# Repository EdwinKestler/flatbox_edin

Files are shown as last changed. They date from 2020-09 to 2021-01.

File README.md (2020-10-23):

# flatbox_edin
Remote math inclusive education for the vision impaired

This is our first attempt to bring remote math edcuation to vision impaired persons. 

#IoT to empower humans. 

Hardware: Raspberry pi 4, 4GB Gateway paired via Wifi to Haptic interfase (drv2603) with response mechanism (MAX6817 de bounce) (vibration motors and push buttons) 2 units. 
IoT: JSON, MQTT, WiFi.
Software: Rabbit MQ, Node-Red, Maria DB, Node.js Angular 9
Cloud: Goolge cloud-> BigQuery, Pub/Sub, Cloud Functions (python and Node.js) 

Main Idea: so a teacher can remotely teach math  to many vision imparied studentes. 1 to many or 1 to 1, via the internet and aremote conference call
Techers interface:
Watch the video (https://youtu.be/AhM5wchl2cA)
Basic Hardware interface:
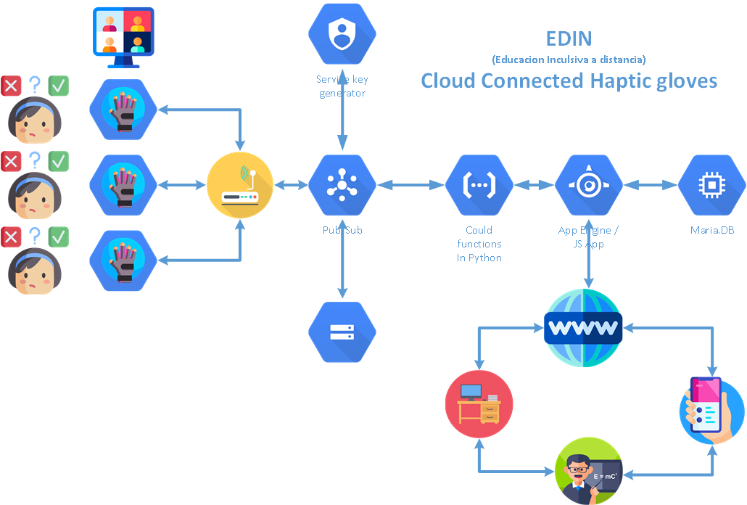
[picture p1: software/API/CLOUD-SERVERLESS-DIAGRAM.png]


Licencing:

Software: 


Hardware: License: <tspan y="0" x="71.357224" id="tspan1179">CERN-OHL-1.2</tspan></text></g></g><text id="text1788" y="-45.219803" x="138.91757" style="font-style:normal;font-weight:normal;font-size:40.0001px;line-height:1.25;font-family:sans-serif;fill:#000000;fill-opacity:1;stroke:none;stroke-width:1" xml:space="preserve">
  
Documentation: 


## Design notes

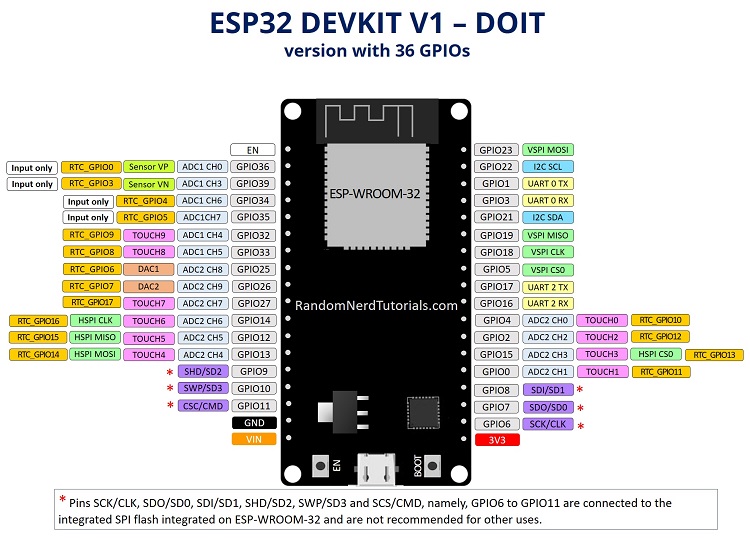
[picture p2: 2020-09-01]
imagenes/ESP32-DOIT-DEVKIT-V1-Board-Pinout-36-GPIOs-updated.jpg

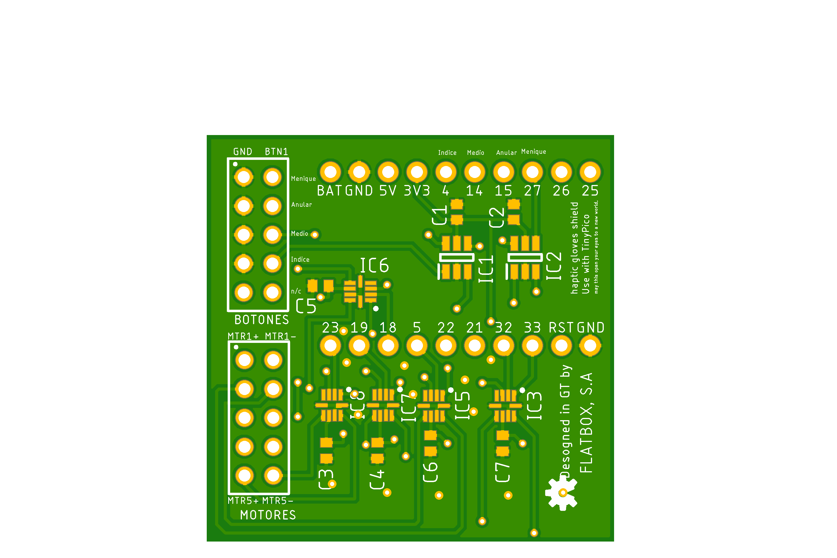
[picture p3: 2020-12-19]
Hardware/Edin_DRV203/Eagle/Shield_Empty.png

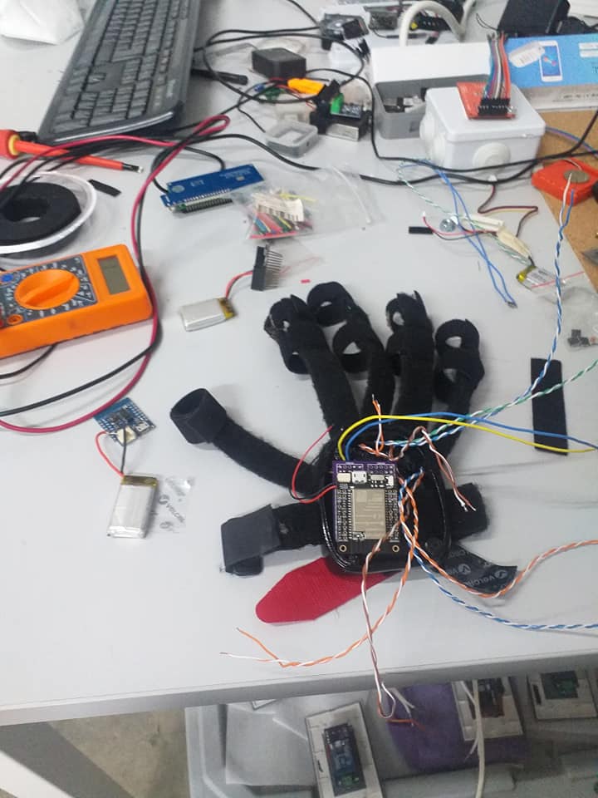
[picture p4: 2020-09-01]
imagenes/117703259_10159825911758132_3864473577027789279_n.jpg

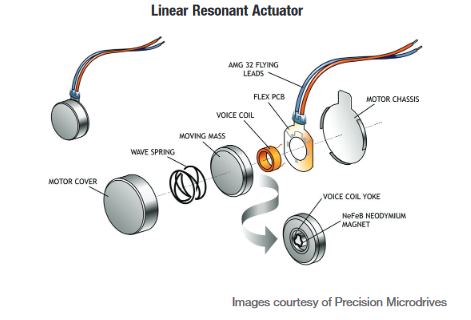
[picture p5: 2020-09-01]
imagenes/haptic-fig-5.webp

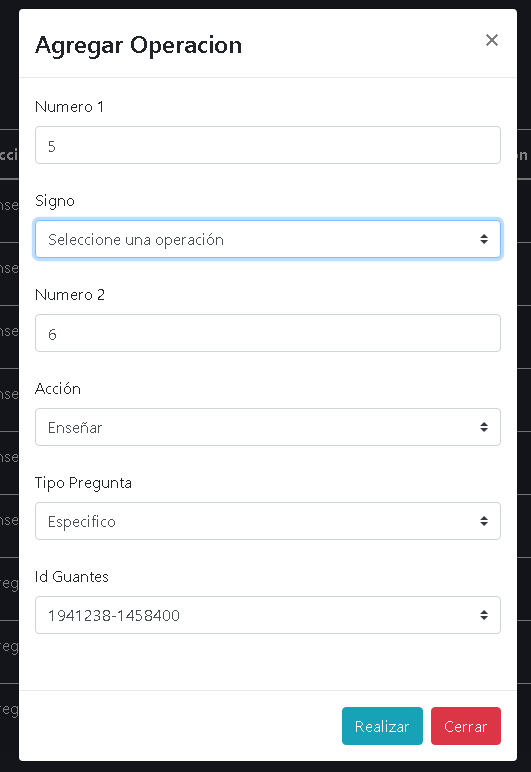
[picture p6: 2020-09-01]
imagenes/operaciones.PNG

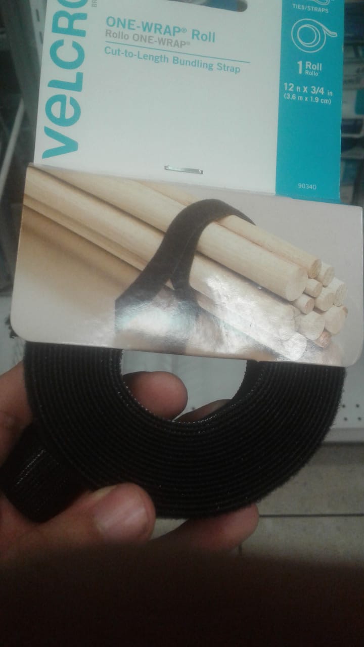
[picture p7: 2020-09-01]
imagenes/b04c229d-c1c4-4ab2-8d0b-719aa09d2a6d.jpg

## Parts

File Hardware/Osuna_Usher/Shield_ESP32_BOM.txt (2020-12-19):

Partlist

Exported from Esp32_Shield.brd at 20/01/2020 19:34

EAGLE Version 9.5.0 Copyright (c) 1988-2019 Autodesk, Inc.

Assembly variant: 

Part     Value                    Package     Library                 Position (mil)        Orientation

BOTONES  BTN 10 PIN               61301021821 Wurth_Connectors_WR-PHD (160 860)             R90
C1_MÑQ   0.1uF                    C0805       resistor                (-950 910)            R90
C2_MDO   0.1uF                    C0805       resistor                (-770 1280)           R180
C3_ANL   0.1uF                    C0805       resistor                (-60 1650)            R180
C4_PLG   0.1uF                    C0805       resistor                (-560 920)            R90
C5_IND   0.1uF                    C0805       resistor                (-960 1220)           R270
D1_B     BLUE                     LED-1206    SparkFun-LED            (-1090 1110)          R180
D2_ANL   1N4148WS                 SOD-323     Diodes                  (-130 1430)           R270
D2_G     GREEN                    LED-1206    SparkFun-LED            (-1090 1030)          R180
D2_MÑQ   1N4148WS                 SOD-323     Diodes                  (-760 980)            R0
D2_PLG   1N4148WS                 SOD-323     Diodes                  (-390 980)            R0
D3_IND   1N4148WS                 SOD-323     Diodes                  (-790 1060)           R0
D3_MDO   1N4148WS                 SOD-323     Diodes                  (-570 1180)           R0
D3_R     RED                      LED-1206    SparkFun-LED            (-1090 950)           R180
MOTORES  MTR 10 PIN               61301021821 Wurth_Connectors_WR-PHD (160 1500)            R270
R1       1K                       R0805       resistor                (-1230 1490)          R90
R2       1K                       R0805       resistor                (-950 1480)           R90
R3       1K                       R0805       resistor                (-650 1480)           R90
R4       1K                       R0805       resistor                (-420 1480)           R90
R5       1K                       R0805       resistor                (-390 1180)           R270
R6_IND   1K                       R0805       resistor                (-780 1160)           R180
R6_R     220                      R0805       resistor                (-1190 870)           R0
R7_G     220                      R0805       resistor                (-1190 1300)          R0
R7_PLG   1K                       R0805       resistor                (-380 890)            R180
R8_B     220                      R0805       resistor                (-1190 1210)          R0
R8_MÑQ   1K                       R0805       resistor                (-760 880)            R180
R9_MDO   1K                       R0805       resistor                (-570 1280)           R180
R10_ANL  1K                       R0805       resistor                (-20 1440)            R90
R13_MÑQ  10K                      R0805       resistor                (-110 600)            R0
R14_MDO  10K                      R0805       resistor                (-110 860)            R0
R15_IND  10K                      R0805       resistor                (-110 990)            R0
R16_ANL  10K                      R0805       resistor                (-110 730)            R0
R17_PLG  10K                      R0805       resistor                (-110 1120)           R0
SV5      ESP32 2x10 PIN_DERECHO   61302021821 Wurth_Connectors_WR-PHD (-750 1700)           R180
SV6      ESP32 2x10 PIN_IZQUIERDO 61302021821 Wurth_Connectors_WR-PHD (-750 700)            R180
T1       600mA/40V                SOT23-3     SparkFun-DiscreteSemi   (-1110 1420)          R270
T2       600mA/40V                SOT23-3     SparkFun-DiscreteSemi   (-830 1400)           R270
T3       600mA/40V                SOT23-3     SparkFun-DiscreteSemi   (-540 1400)           R270
T4       600mA/40V                SOT23-3     SparkFun-DiscreteSemi   (-300 1400)           R270
T5       600mA/40V                SOT23-3     SparkFun-DiscreteSemi   (-260 1260)           R0

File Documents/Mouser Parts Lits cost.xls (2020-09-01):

EDIN-USHERV2.0
Mouser # | Mfr. # | Manufacturer | Customer # | Description | RoHS | Lifecycle | Order Qty. | Price (USD) | Ext.: (USD)
581-06031C104KAT2A | 06031C104KAT2A | AVX |  | Multilayer Ceramic Capacitors MLCC - SMD/SMT 100V 0.1uF 0603 X7R 10% | RoHS Compliant |  | 2 | $0.19 | $0.38
791-0603B104K160CT | 0603B104K160CT | Walsin |  | Multilayer Ceramic Capacitors MLCC - SMD/SMT 0.1uF 16V 10% 0805 X7R | RoHS Compliant | New At Mouser | 5 | $0.10 | $0.50
700-MAX6817EUTT | MAX6817EUT+T | Maxim Integrated |  | Supervisory Circuits A +/- 15kV ESD-Protected, Single/Dual/Octal, CMOS Switch Debouncers | RoHS Compliant |  | 2 | $4.32 | $8.64
595-DRV2603RUNR | DRV2603RUNR | Texas Instruments |  | Motor / Motion / Ignition Controllers & Drivers Haptic Driver w/Auto Resonance Tracking | RoHS Compliant |  | 5 | $1.31 | $6.55

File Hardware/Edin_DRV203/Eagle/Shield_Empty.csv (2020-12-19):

Qty | Value | Device | Package | Parts | Description | DATASHEET-URL | DESCRIPTION | GENDER | HEIGHT | IR | MANUFACTURER_NAME | MANUFACTURER_PART_NUMBER | MATES | MOUSER_PART_NUMBER | MOUSER_PRICE-STOCK | PACKAGING | PART-NUMBER | PINS | PROD_ID | ROWS | TYPE
2 |  | TINYPICO_HEADER_10NO_SILK_PTH_FEMALE | 1X10_NO_SILK | LEFT, RIGHT | Multi connection point. Often used as Generic Header-pin footprint for 0.1 inch spaced/style header connections |  |  |  |  |  |  |  |  |  |  |  |  |  | CONN-11563
5 | 06031C104KAT2A | 06031C104KAT2A | CAPC1608X90N | C3, C4, C5, C6, C7 | AVX - 06031C104KAT2A - CAP, MLCC, X7R, 0.1UF, 100V, 0603 |  | AVX - 06031C104KAT2A - CAP, MLCC, X7R, 0.1UF, 100V, 0603 |  | 0.9mm |  | AVX | 06031C104KAT2A |  | 581-06031C104KAT2A | https://www.mouser.co.uk/ProductDetail/AVX/06031C104KAT2A?qs=oF%2FSscNnLpBUv12UcNAw2A%3D%3D
2 | 0603B104K160CT | 0603B104K160CT | CAPC1608X87N | C1, C2 | WALSIN - 0603B104K160CT - CAP, 0.1F, 16V, 10%, X7R, 0603 |  | WALSIN - 0603B104K160CT - CAP, 0.1F, 16V, 10%, X7R, 0603 |  | 0.87mm |  | Walsin Technology Corporation | 0603B104K160CT |  | 791-0603B104K160CT | https://www.mouser.com/Search/Refine.aspx?Keyword=791-0603B104K160CT
1 | BTN 10 PIN | 6130XX21821_61301021821 | 61301021821 | BOTONES | WR-PHD 2.54 mm Dual Socket Header | https://katalog.we-online.com/em/datasheet/61301021821.pdf |  | Socket Header |  | 3A |  |  | WR-PHD 2.54mm SMT Dual Pin Header/THT Angled Dual Pin Header/THT Dual Board Stacker/THT Dual Pin Header |  |  | Tray | 61301021821 | 10 |  | Dual | Straight
5 | DRV2603RUNR | DRV2603RUNR | QFN50P200X200X80-10N | IC3, IC5, IC6, IC7, IC8 | Haptic Driver with Auto Resonance Tracking for LRA and Optimized Drive for ERM |  | Haptic Driver with Auto Resonance Tracking for LRA and Optimized Drive for ERM |  | 0.8mm |  | Texas Instruments | DRV2603RUNR |  | 595-DRV2603RUNR | https://www.mouser.co.uk/ProductDetail/Texas-Instruments/DRV2603RUNR?qs=l6ZoeTYLMwNhoGl8Q31%2FaA%3D%3D
2 | MAX6817EUT+T | MAX6817EUT+T | SOT95P280X145-6N | IC1, IC2 | Supervisory Circuits Dual Switch Debouncer |  | Supervisory Circuits Dual Switch Debouncer |  | 1.45mm |  | Maxim Integrated | MAX6817EUT+T |  | 700-MAX6817EUTT | https://www.mouser.co.uk/ProductDetail/Maxim-Integrated/MAX6817EUT%2bT?qs=1THa7WoU59HkU%2FfQtsyW%252BA%3D%3D
1 | MTR 10 PIN | 6130XX21821_61301021821 | 61301021821 | MOTORES | WR-PHD 2.54 mm Dual Socket Header | https://katalog.we-online.com/em/datasheet/61301021821.pdf |  | Socket Header |  | 3A |  |  | WR-PHD 2.54mm SMT Dual Pin Header/THT Angled Dual Pin Header/THT Dual Board Stacker/THT Dual Pin Header |  |  | Tray | 61301021821 | 10 |  | Dual | Straight
1 | OSHW-LOGOS | OSHW-LOGOS | OSHW-LOGO-S | LOGO1 | Open-Source Hardware (OSHW) Logo

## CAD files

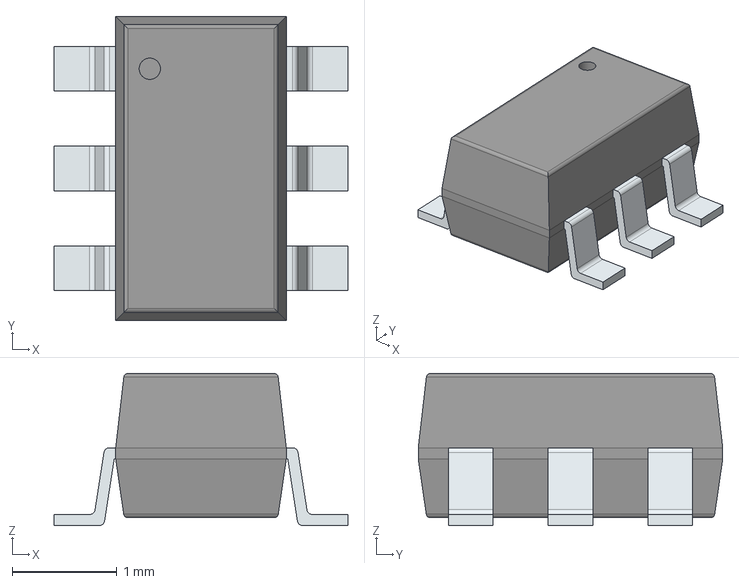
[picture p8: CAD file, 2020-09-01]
EcadModels/MAX6817EUT+T/3D/MAX6817EUT+T.stp
2.80 x 2.90 x 1.45 mm
PinsArrayLR

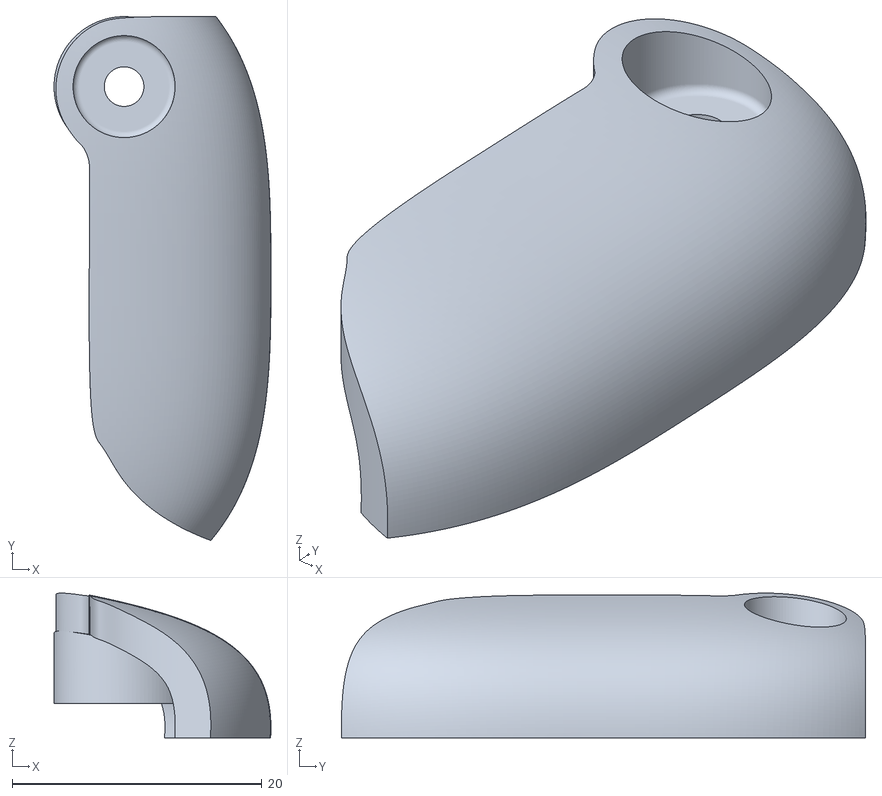
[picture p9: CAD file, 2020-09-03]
Fusion Models/EDIN_Tapadera.stl
17.4 x 42.0 x 11.6

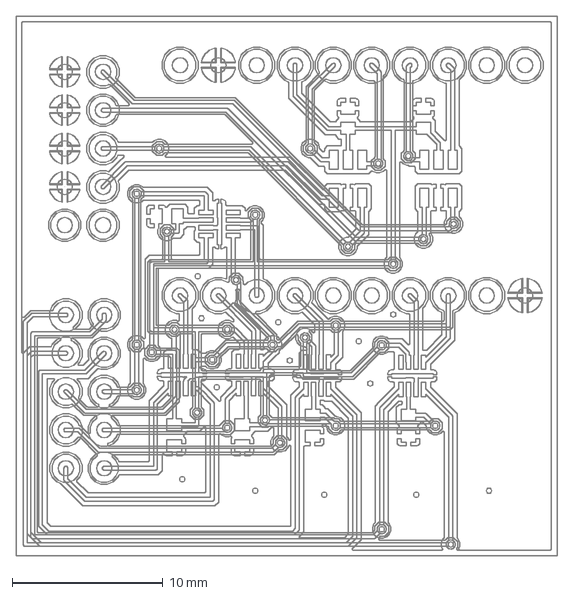
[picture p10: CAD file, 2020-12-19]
Hardware/Edin_DRV203/Eagle/Shield_Empty.dxf
35.9 x 35.8 mm

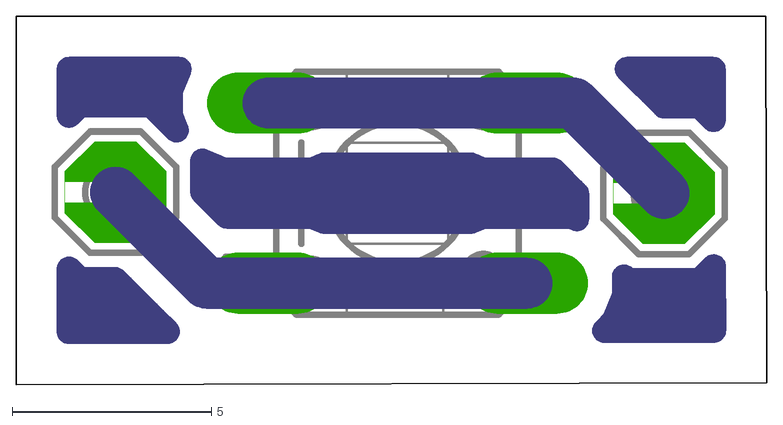
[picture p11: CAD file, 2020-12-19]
Hardware/Osuna_Usher/button_fingers2.dxf
18.8 x 9.24

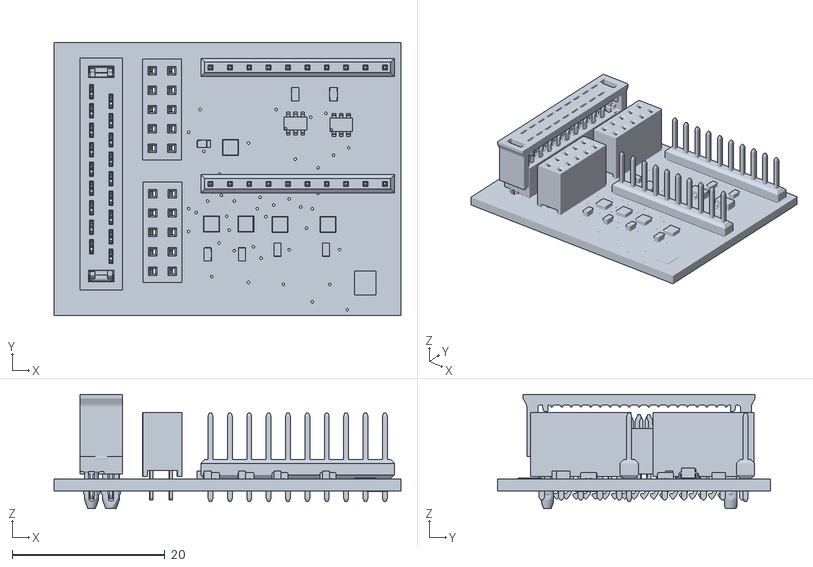
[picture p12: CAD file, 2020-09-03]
Fusion Models/Shield_Empty.stl
45.5 x 35.8 x 14.9

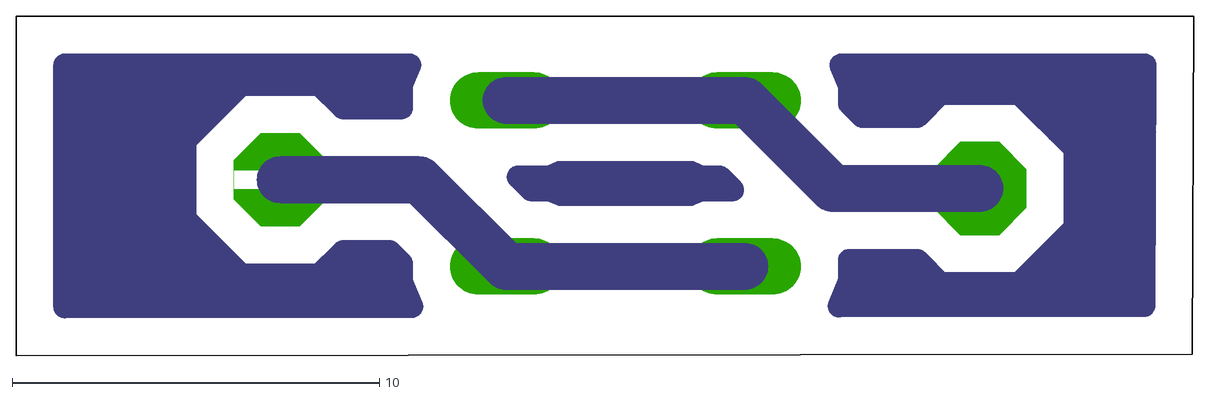
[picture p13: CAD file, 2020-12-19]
Hardware/Osuna_Usher/button_fingers.dxf
32.1 x 9.24

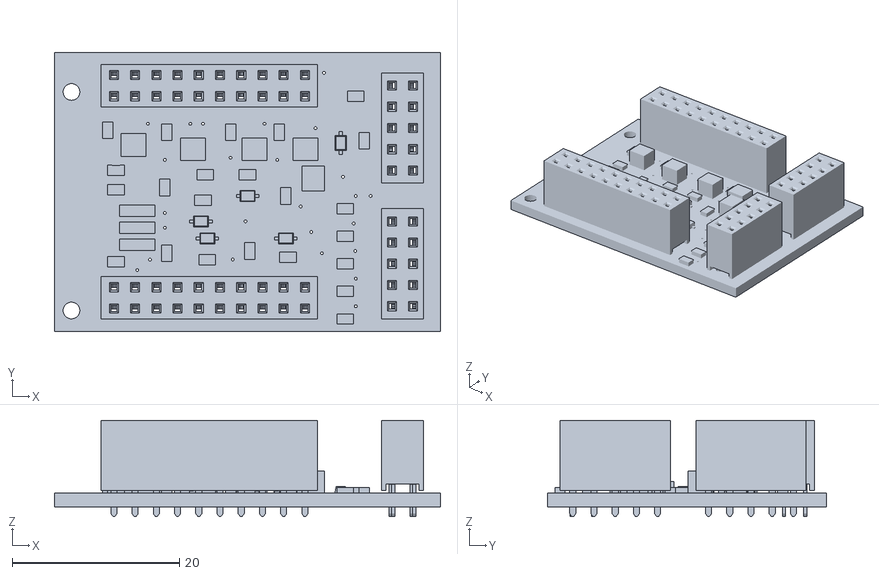
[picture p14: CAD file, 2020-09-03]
Fusion Models/Esp32_Shield.stl
46.2 x 33.5 x 11.5

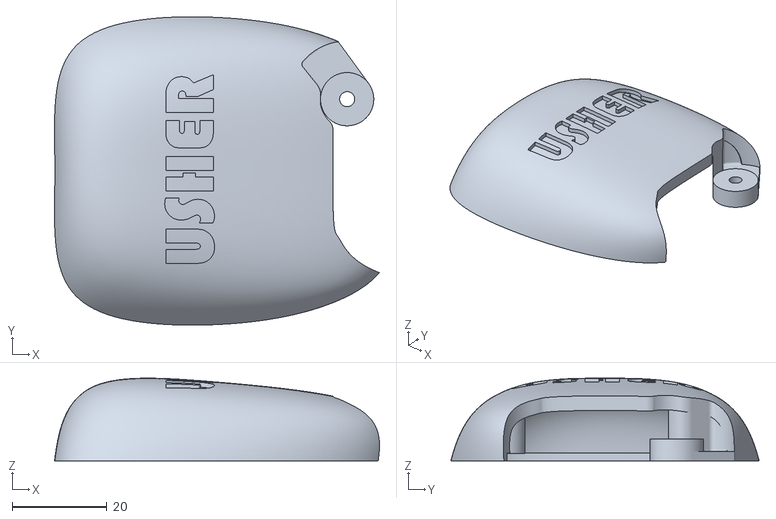
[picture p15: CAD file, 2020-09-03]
Fusion Models/EDIN_tapa.stl
68.4 x 64.9 x 17.4

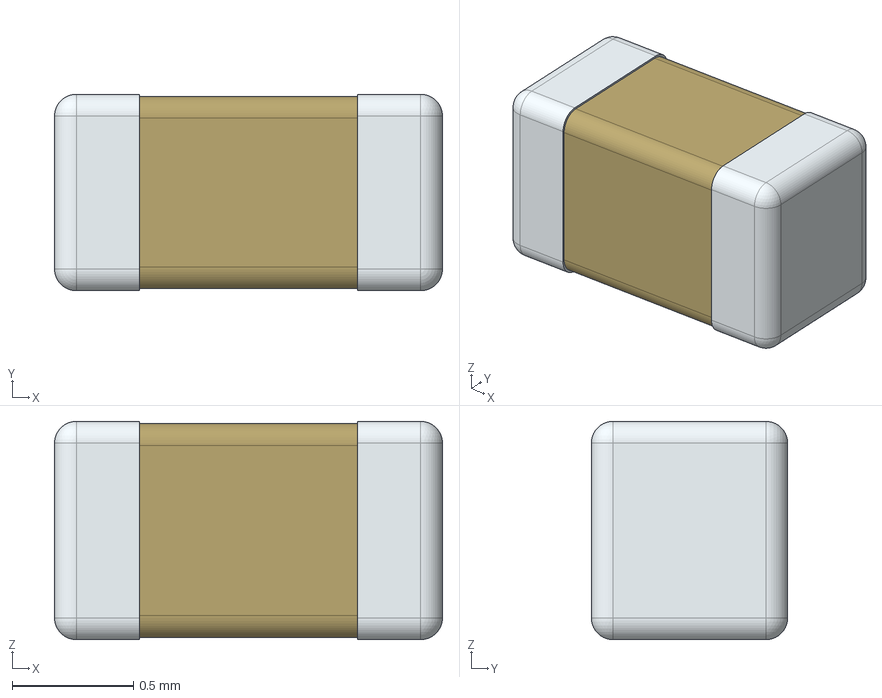
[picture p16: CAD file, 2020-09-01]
EcadModels/06031C104KAT2A/3D/06031C104KAT2A.stp
1.60 x 0.81 x 0.9 mm

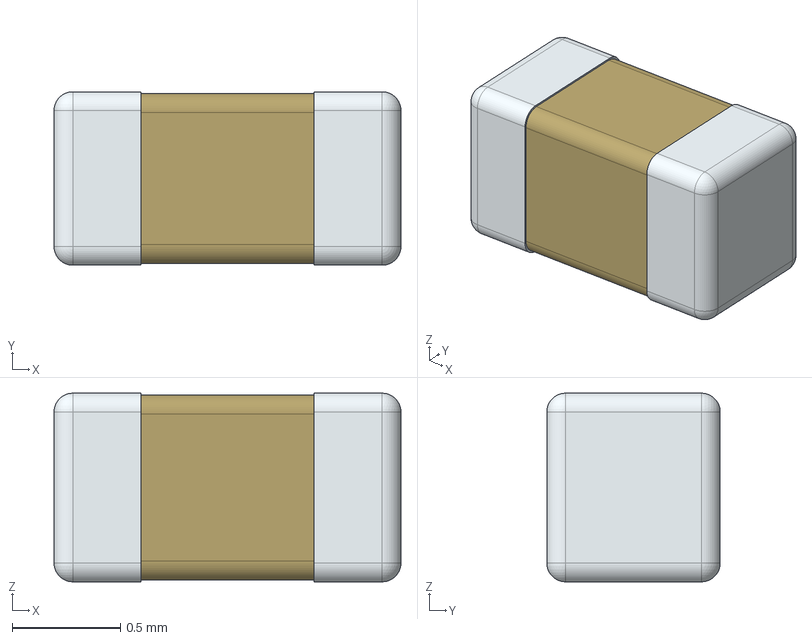
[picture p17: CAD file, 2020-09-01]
EcadModels/0603B104K160CT/3D/0603B104K160CT.stp
1.60 x 0.8 x 0.87 mm

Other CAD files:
EcadModels/06031C104KAT2A/3D/06031C104KAT2A.stl
EcadModels/0603B104K160CT/3D/0603B104K160CT.stl
EcadModels/MAX6817EUT+T/3D/MAX6817EUT+T.stl

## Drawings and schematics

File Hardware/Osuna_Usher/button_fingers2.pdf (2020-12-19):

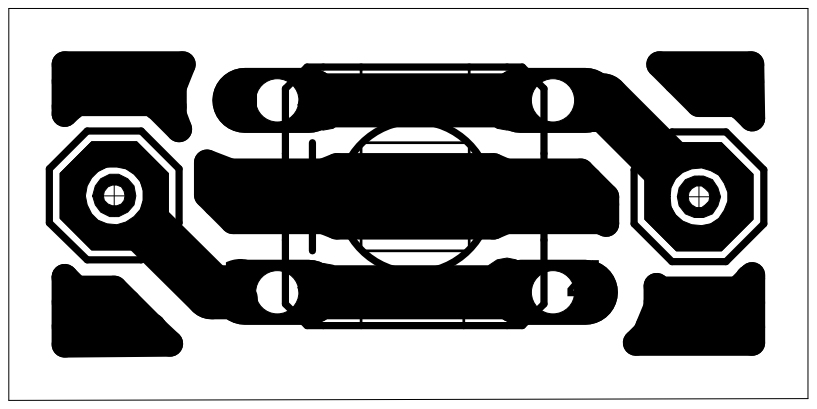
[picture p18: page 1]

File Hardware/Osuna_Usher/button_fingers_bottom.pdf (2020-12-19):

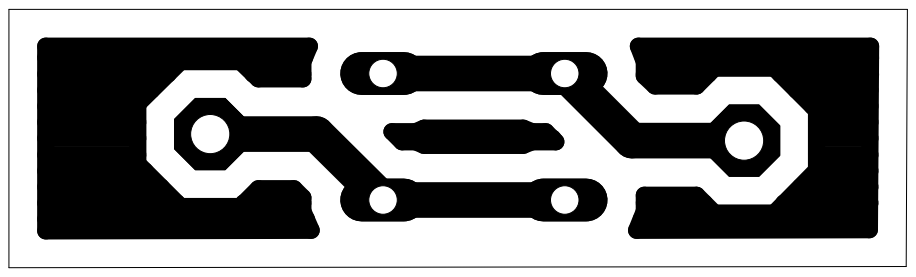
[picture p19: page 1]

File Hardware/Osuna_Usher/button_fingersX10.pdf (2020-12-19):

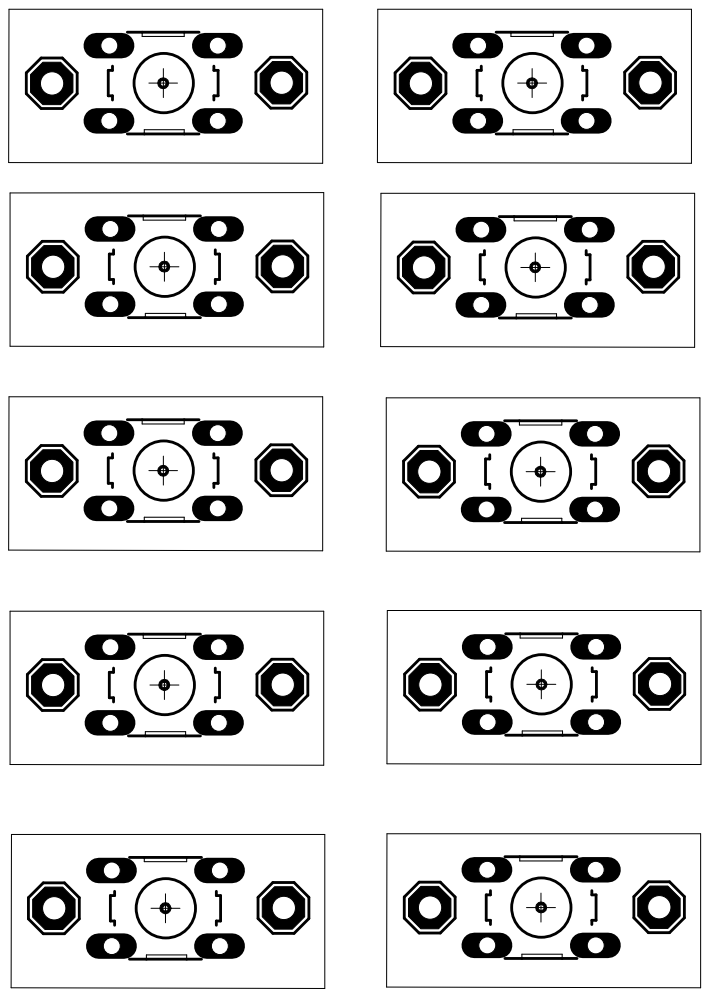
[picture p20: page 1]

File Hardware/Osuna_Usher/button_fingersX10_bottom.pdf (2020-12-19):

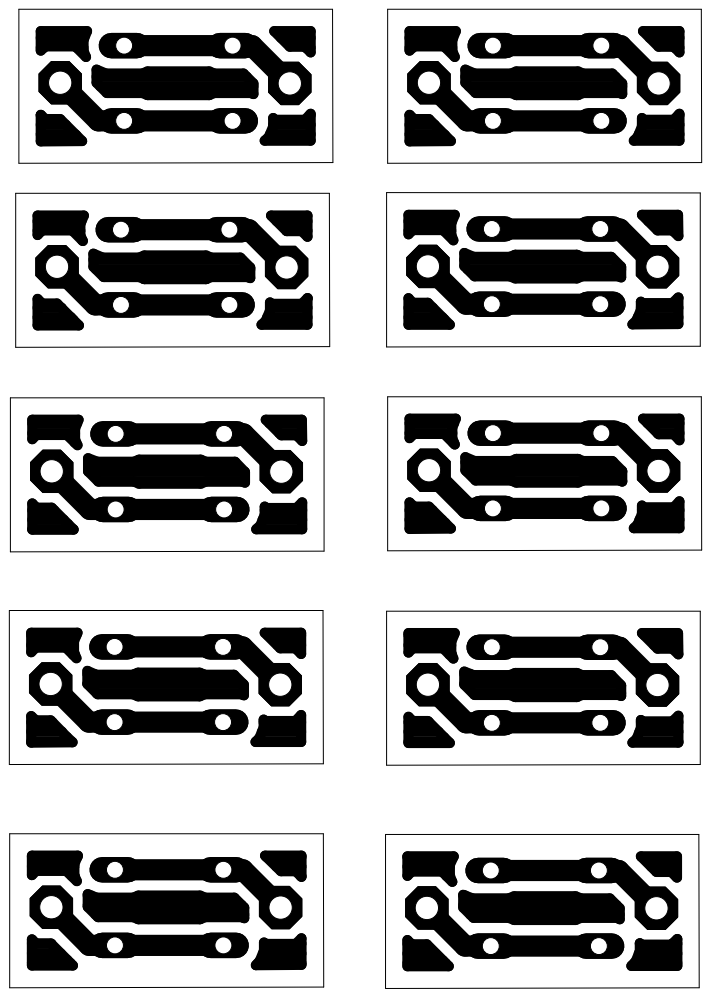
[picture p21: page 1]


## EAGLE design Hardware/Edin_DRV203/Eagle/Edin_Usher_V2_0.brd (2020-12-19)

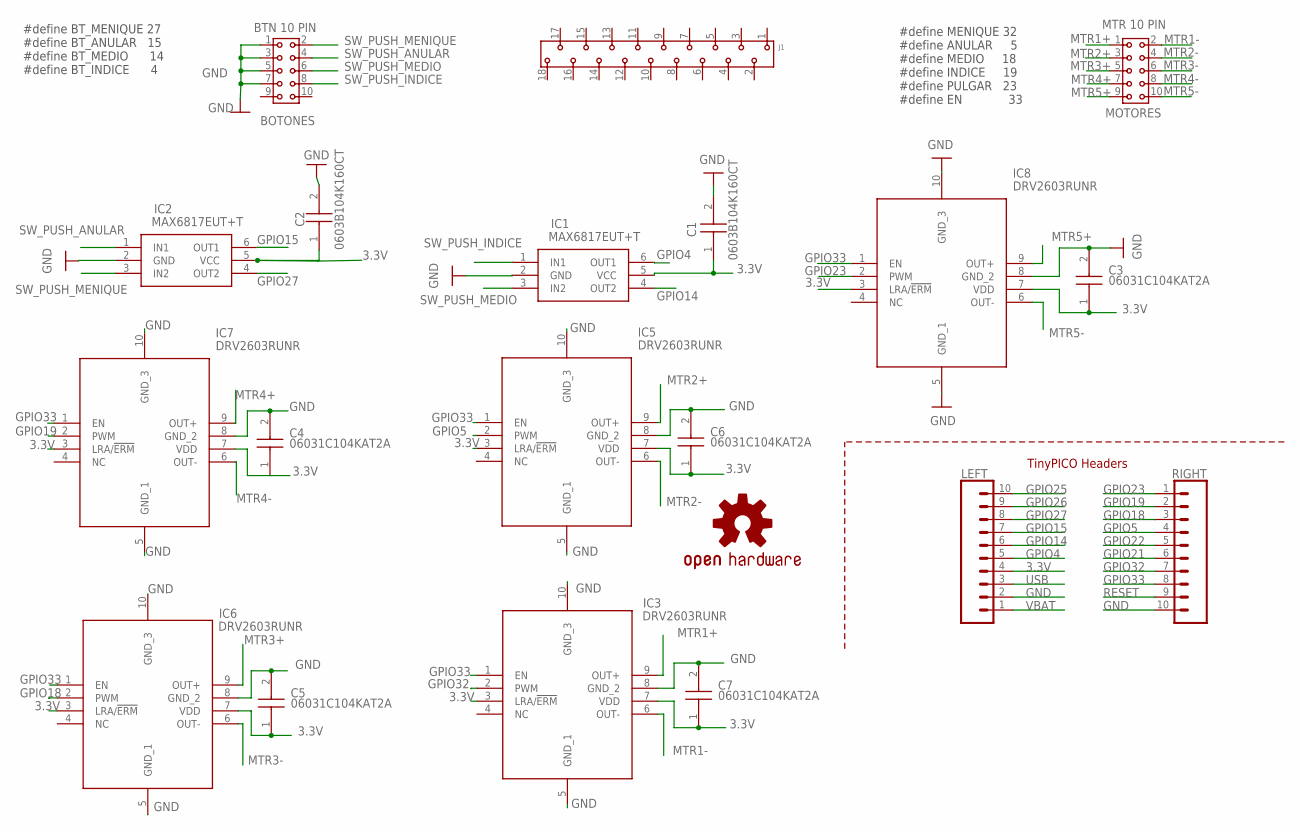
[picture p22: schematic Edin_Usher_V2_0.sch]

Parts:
BOTONES: BTN 10 PIN; 61301021821
C1, C2: 0603B104K160CT; CAPC1608X87N
C3, C4, C5, C6, C7: 06031C104KAT2A; CAPC1608X90N
IC1, IC2: MAX6817EUT+T; SOT95P280X145-6N
IC3, IC5, IC6, IC7, IC8: DRV2603RUNR; QFN50P200X200X80-10N
J1: 490107671812
LEFT: TINYPICO_HEADER_10NO_SILK_PTH_FEMALE; 1X10_NO_SILK
LOGO1: OSHW-LOGOS; OSHW-LOGO-S
MOTORES: MTR 10 PIN; 61301021821
RIGHT: TINYPICO_HEADER_10NO_SILK_PTH_FEMALE; 1X10_NO_SILK

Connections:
3.3V: C1.1, C2.1, C3.1, C4.1, C5.1, C6.1, C7.1, IC1.5 (VCC), IC2.5 (VCC), IC3.3 (LRA/!ERM), IC3.7 (VDD), IC5.3 (LRA/!ERM), IC5.7 (VDD), IC6.3 (LRA/!ERM), IC6.7 (VDD), IC7.3 (LRA/!ERM), IC7.7 (VDD), IC8.3 (LRA/!ERM), IC8.7 (VDD), LEFT.4
GND: BOTONES.1, BOTONES.3, BOTONES.5, BOTONES.7, C1.2, C2.2, C3.2, C4.2, C5.2, C6.2, C7.2, IC1.2 (GND), IC2.2 (GND), IC3.5 (GND_1), IC3.8 (GND_2), IC3.10 (GND_3), IC5.5 (GND_1), IC5.8 (GND_2), IC5.10 (GND_3), IC6.5 (GND_1), IC6.8 (GND_2), IC6.10 (GND_3), IC7.5 (GND_1), IC7.8 (GND_2), IC7.10 (GND_3), IC8.5 (GND_1), IC8.8 (GND_2), IC8.10 (GND_3), LEFT.2, RIGHT.10
GPIO4: IC1.6 (OUT1), LEFT.5
GPIO5: IC5.2 (PWM), RIGHT.4
GPIO14: IC1.4 (OUT2), LEFT.6
GPIO15: IC2.6 (OUT1), LEFT.7
GPIO18: IC6.2 (PWM), RIGHT.3
GPIO19: IC7.2 (PWM), RIGHT.2
GPIO21: RIGHT.6
GPIO22: RIGHT.5
GPIO23: IC8.2 (PWM), RIGHT.1
GPIO25: LEFT.10
GPIO26: LEFT.9
GPIO27: IC2.4 (OUT2), LEFT.8
GPIO32: IC3.2 (PWM), RIGHT.7
GPIO33: IC3.1 (EN), IC5.1 (EN), IC6.1 (EN), IC7.1 (EN), IC8.1 (EN), RIGHT.8
MTR1+: IC3.9 (OUT+), MOTORES.1
MTR1-: IC3.6 (OUT-), MOTORES.2
MTR2+: IC5.9 (OUT+), MOTORES.3
MTR2-: IC5.6 (OUT-), MOTORES.4
MTR3+: IC6.9 (OUT+), MOTORES.5
MTR3-: IC6.6 (OUT-), MOTORES.6
MTR4+: IC7.9 (OUT+), MOTORES.7
MTR4-: IC7.6 (OUT-), MOTORES.8
MTR5+: IC8.9 (OUT+), MOTORES.9
MTR5-: IC8.6 (OUT-), MOTORES.10
RESET: RIGHT.9
SW_PUSH_ANULAR: BOTONES.4, IC2.1 (IN1)
SW_PUSH_INDICE: BOTONES.8, IC1.1 (IN1)
SW_PUSH_MEDIO: BOTONES.6, IC1.3 (IN2)
SW_PUSH_MENIQUE: BOTONES.2, IC2.3 (IN2)
USB: LEFT.3
VBAT: LEFT.1

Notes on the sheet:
TinyPICO Headers
#define MENIQUE 32 #define ANULAR 5 #define MEDIO 18 #define INDICE 19 #define PULGAR 23 #define EN 33
#define BT_MENIQUE 27 #define BT_ANULAR 15 #define BT_MEDIO 14 #define BT_INDICE 4

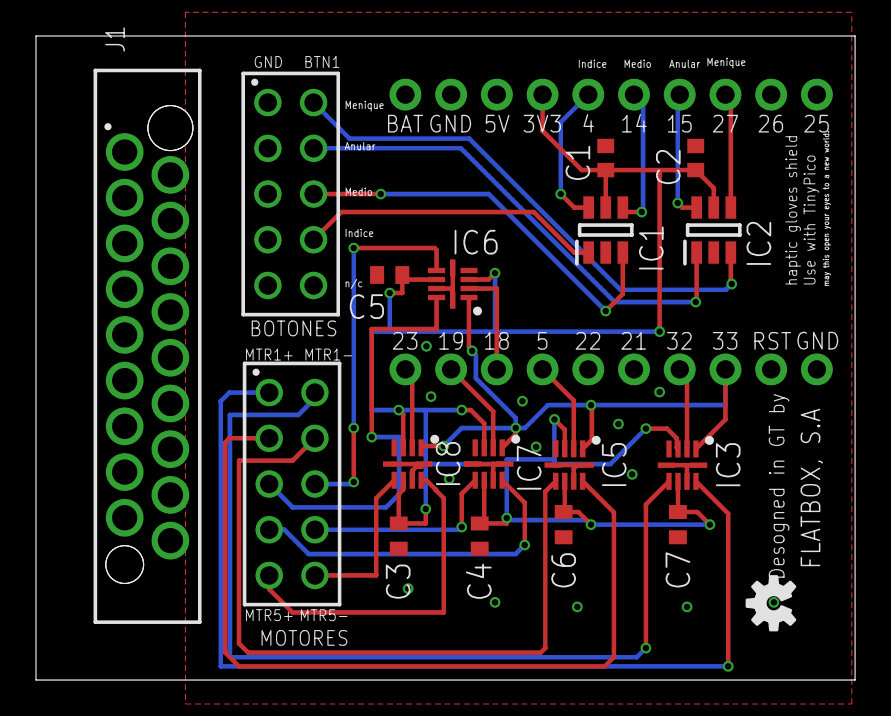
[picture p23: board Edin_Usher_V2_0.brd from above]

Board: 2 copper layers, 45.5 x 35.8 mm, 21 parts (1 on the bottom side), 26 nets.

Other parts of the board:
LOGO2: OSHW-LOGOS; OSHW-LOGO-S

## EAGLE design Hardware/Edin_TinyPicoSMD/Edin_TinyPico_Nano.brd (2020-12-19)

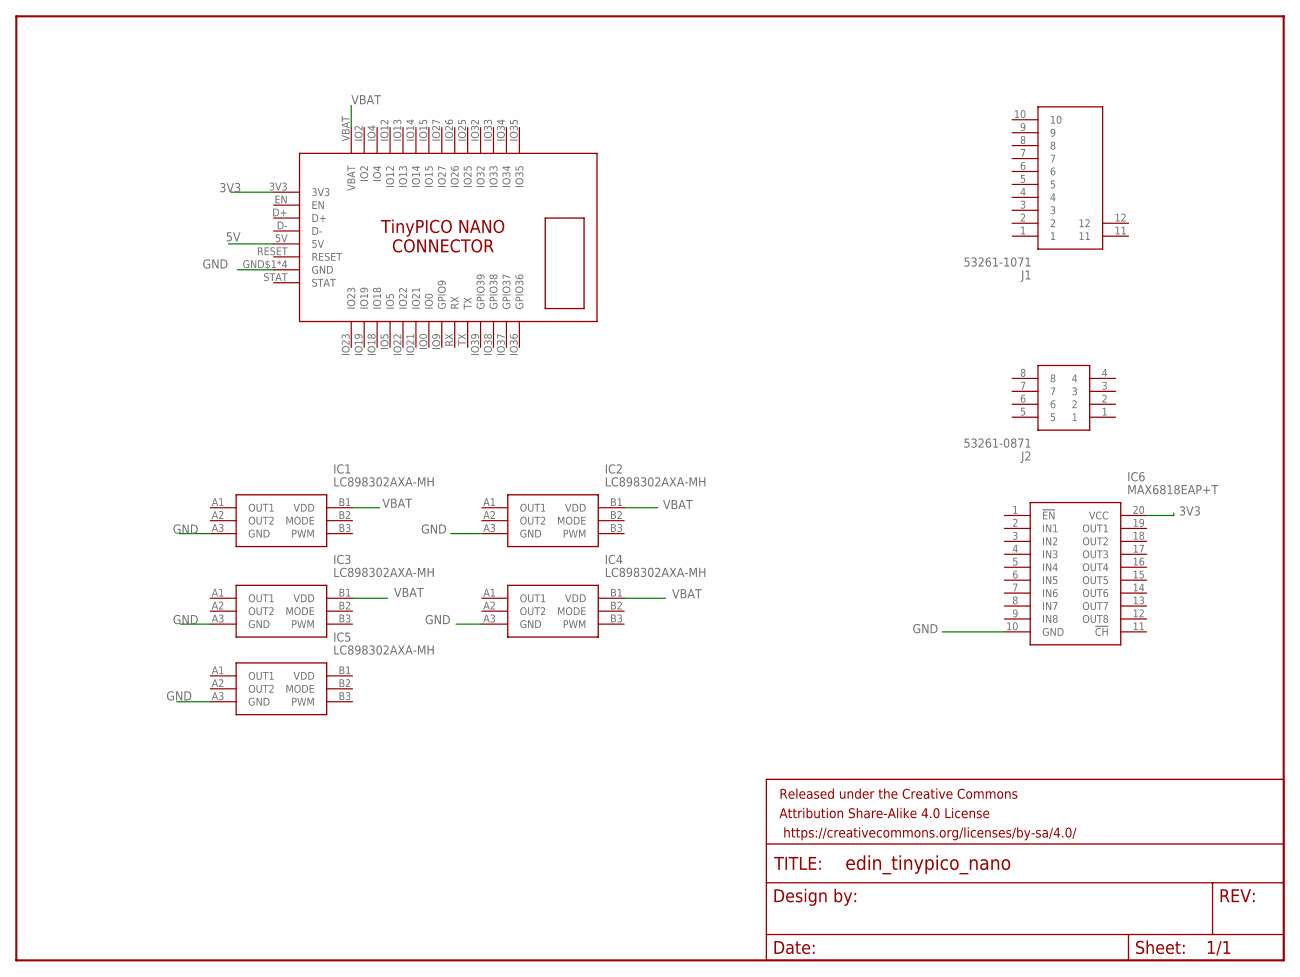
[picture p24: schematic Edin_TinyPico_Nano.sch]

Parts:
FRAME1: FRAME-LETTER; CREATIVE_COMMONS
IC1, IC2, IC3, IC4, IC5: LC898302AXA-MH; BGA6C40P3X2_118X78X65
IC6: MAX6818EAP+T; SOP65P778X199-20N
J1: 53261-1071; 532611071
J2: 53261-0871
U$1: TINYPICO-NANO-CONNECTOR

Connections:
3V3: IC6.20 (VCC), U$1.3V3
5V: U$1.5V
GND: IC1.A3 (GND), IC2.A3 (GND), IC3.A3 (GND), IC4.A3 (GND), IC5.A3 (GND), IC6.10 (GND), U$1.GND$1 (GND), U$1.GND$2 (GND), U$1.GND$3 (GND), U$1.GND$4 (GND)
VBAT: IC1.B1 (VDD), IC2.B1 (VDD), IC3.B1 (VDD), IC4.B1 (VDD), U$1.VBAT

Board: 2 copper layers, 10 parts (0 on the bottom side), 3 nets, no tracks yet.

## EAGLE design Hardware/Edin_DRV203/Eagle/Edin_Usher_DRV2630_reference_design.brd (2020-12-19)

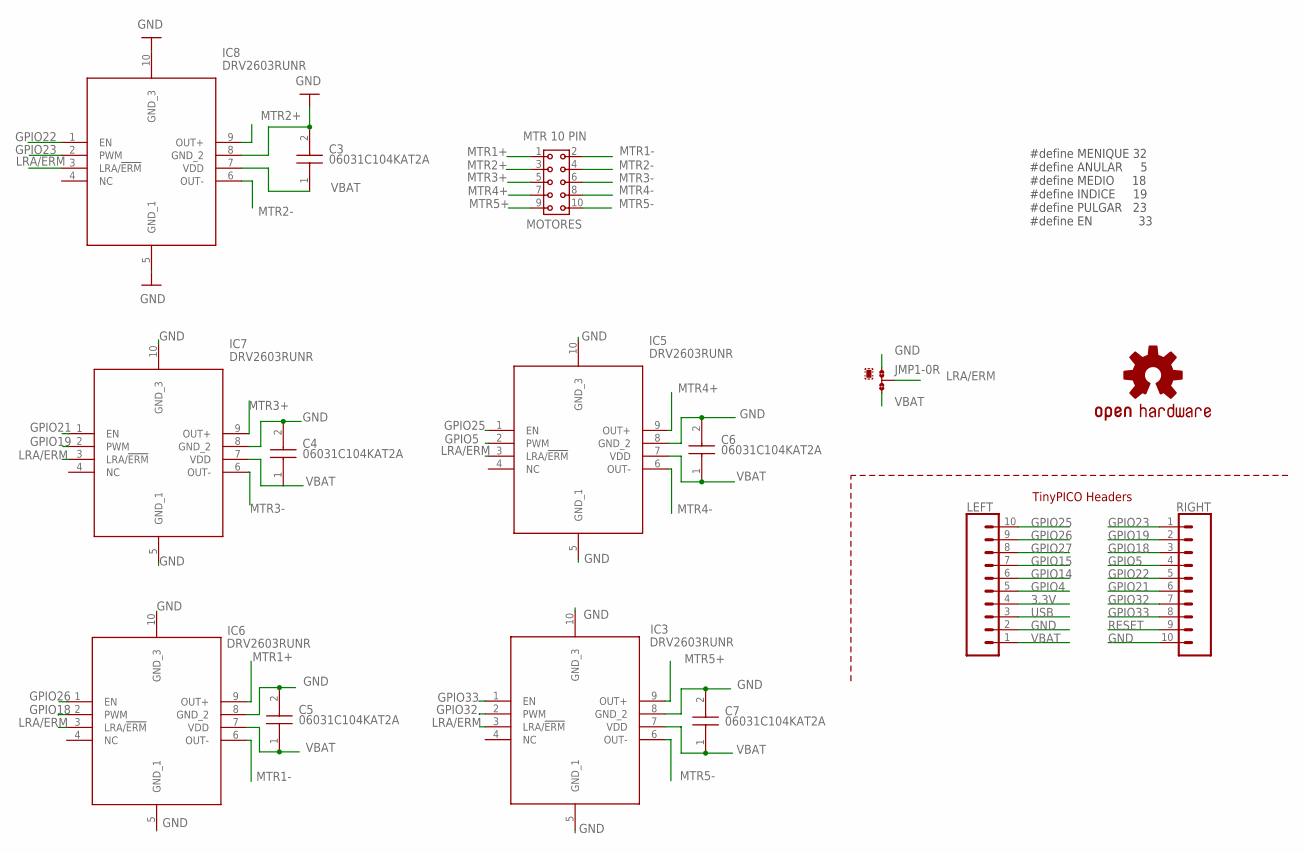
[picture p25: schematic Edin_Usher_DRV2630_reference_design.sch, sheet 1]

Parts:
C3, C4, C5, C6, C7: 06031C104KAT2A; CAPC1608X90N
IC3, IC5, IC6, IC7, IC8: DRV2603RUNR; QFN50P200X200X80-10N
JMP1: 0R-JUMPA; A0R-JMP
LEFT: TINYPICO_HEADER_10NO_SILK_PTH_FEMALE; 1X10_NO_SILK
LOGO1: OSHW-LOGOS; OSHW-LOGO-S
MOTORES: MTR 10 PIN; 61301021821
RIGHT: TINYPICO_HEADER_10NO_SILK_PTH_FEMALE; 1X10_NO_SILK

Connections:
3.3V: LEFT.4; also elsewhere on the board
GND: C3.2, C4.2, C5.2, C6.2, C7.2, IC3.5 (GND_1), IC3.8 (GND_2), IC3.10 (GND_3), IC5.5 (GND_1), IC5.8 (GND_2), IC5.10 (GND_3), IC6.5 (GND_1), IC6.8 (GND_2), IC6.10 (GND_3), IC7.5 (GND_1), IC7.8 (GND_2), IC7.10 (GND_3), IC8.5 (GND_1), IC8.8 (GND_2), IC8.10 (GND_3), JMP1.1, LEFT.2, RIGHT.10; also elsewhere on the board
GPIO4: LEFT.5; also elsewhere on the board
GPIO5: IC5.2 (PWM), RIGHT.4
GPIO14: LEFT.6; also elsewhere on the board
GPIO15: LEFT.7; also elsewhere on the board
GPIO18: IC6.2 (PWM), RIGHT.3
GPIO19: IC7.2 (PWM), RIGHT.2
GPIO21: IC7.1 (EN), RIGHT.6
GPIO22: IC8.1 (EN), RIGHT.5
GPIO23: IC8.2 (PWM), RIGHT.1
GPIO25: IC5.1 (EN), LEFT.10
GPIO26: IC6.1 (EN), LEFT.9
GPIO27: LEFT.8; also elsewhere on the board
GPIO32: IC3.2 (PWM), RIGHT.7
GPIO33: IC3.1 (EN), RIGHT.8
LRA/ERM: IC3.3 (LRA/!ERM), IC5.3 (LRA/!ERM), IC6.3 (LRA/!ERM), IC7.3 (LRA/!ERM), IC8.3 (LRA/!ERM), JMP1.2
MTR1+: IC6.9 (OUT+), MOTORES.1
MTR1-: IC6.6 (OUT-), MOTORES.2
MTR2+: IC8.9 (OUT+), MOTORES.3
MTR2-: IC8.6 (OUT-), MOTORES.4
MTR3+: IC7.9 (OUT+), MOTORES.5
MTR3-: IC7.6 (OUT-), MOTORES.6
MTR4+: IC5.9 (OUT+), MOTORES.7
MTR4-: IC5.6 (OUT-), MOTORES.8
MTR5+: IC3.9 (OUT+), MOTORES.9
MTR5-: IC3.6 (OUT-), MOTORES.10
RESET: RIGHT.9; also elsewhere on the board
USB: LEFT.3
VBAT: C3.1, C4.1, C5.1, C6.1, C7.1, IC3.7 (VDD), IC5.7 (VDD), IC6.7 (VDD), IC7.7 (VDD), IC8.7 (VDD), JMP1.3, LEFT.1

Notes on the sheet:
TinyPICO Headers
#define MENIQUE 32 #define ANULAR 5 #define MEDIO 18 #define INDICE 19 #define PULGAR 23 #define EN 33

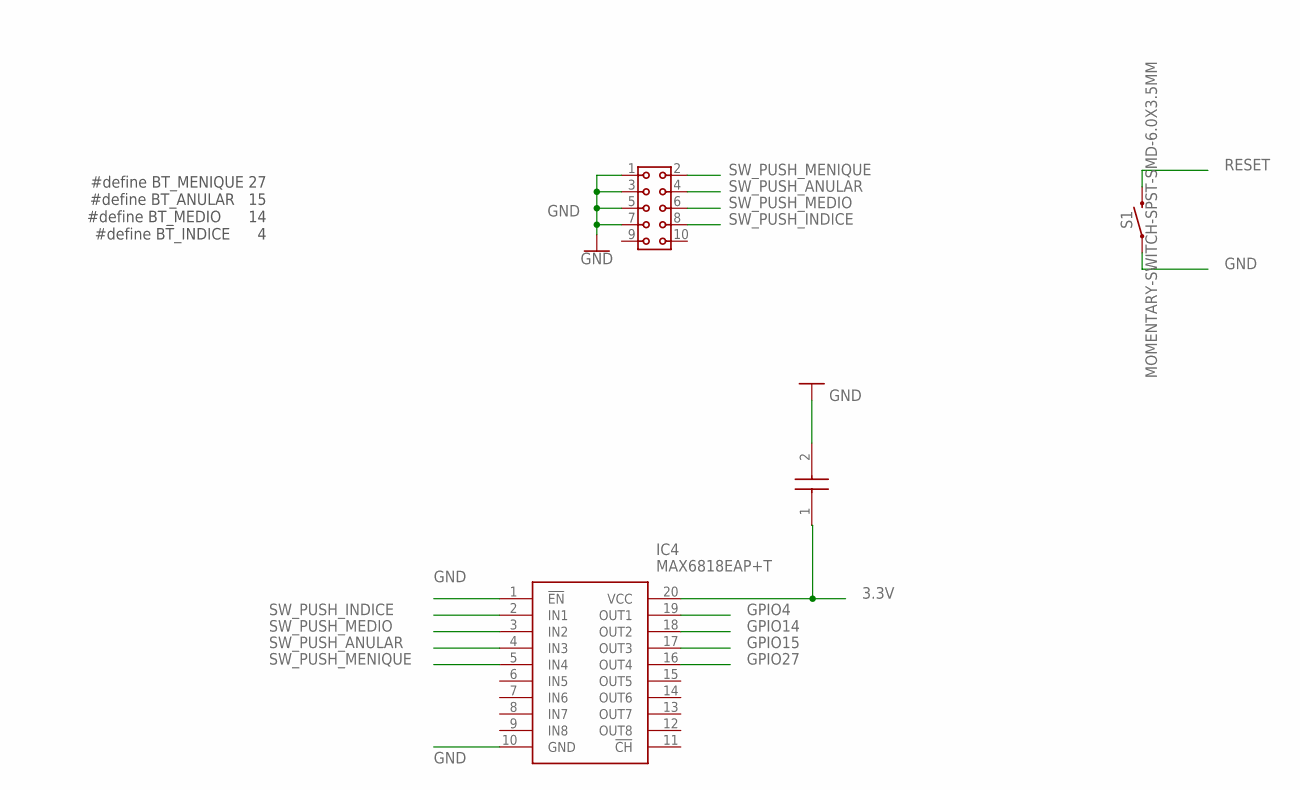
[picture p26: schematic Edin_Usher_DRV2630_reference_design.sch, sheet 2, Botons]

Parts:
BOTONES: BTN 10 PIN; 61301021821
C8: 0603B104K160CT; CAPC1608X87N
IC4: MAX6818EAP+T; SOP65P778X199-20N
S1: MOMENTARY-SWITCH-SPST-SMD-6.0X3.5MM; TACTILE_SWITCH_SMD_6.0X3.5MM

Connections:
3.3V: C8.1, IC4.20 (VCC); also elsewhere on the board
GND: BOTONES.1, BOTONES.3, BOTONES.5, BOTONES.7, C8.2, IC4.1 (!EN), IC4.10 (GND), S1.1; also elsewhere on the board
GPIO4: IC4.19 (OUT1); also elsewhere on the board
GPIO14: IC4.18 (OUT2); also elsewhere on the board
GPIO15: IC4.17 (OUT3); also elsewhere on the board
GPIO27: IC4.16 (OUT4); also elsewhere on the board
RESET: S1.2; also elsewhere on the board
SW_PUSH_ANULAR: BOTONES.4, IC4.4 (IN3)
SW_PUSH_INDICE: BOTONES.8, IC4.2 (IN1)
SW_PUSH_MEDIO: BOTONES.6, IC4.3 (IN2)
SW_PUSH_MENIQUE: BOTONES.2, IC4.5 (IN4)

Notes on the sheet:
#define BT_MENIQUE 27 #define BT_ANULAR 15 #define BT_MEDIO 14 #define BT_INDICE 4

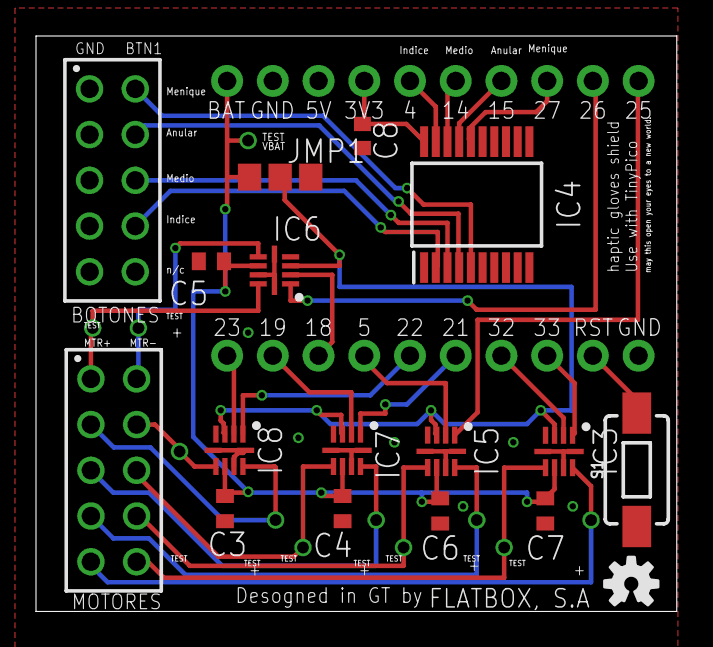
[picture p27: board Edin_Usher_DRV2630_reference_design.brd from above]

Board: 2 copper layers, 35.6 x 32.0 mm, 20 parts (1 on the bottom side), 33 nets.

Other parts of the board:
LOGO2: OSHW-LOGOS; OSHW-LOGO-S

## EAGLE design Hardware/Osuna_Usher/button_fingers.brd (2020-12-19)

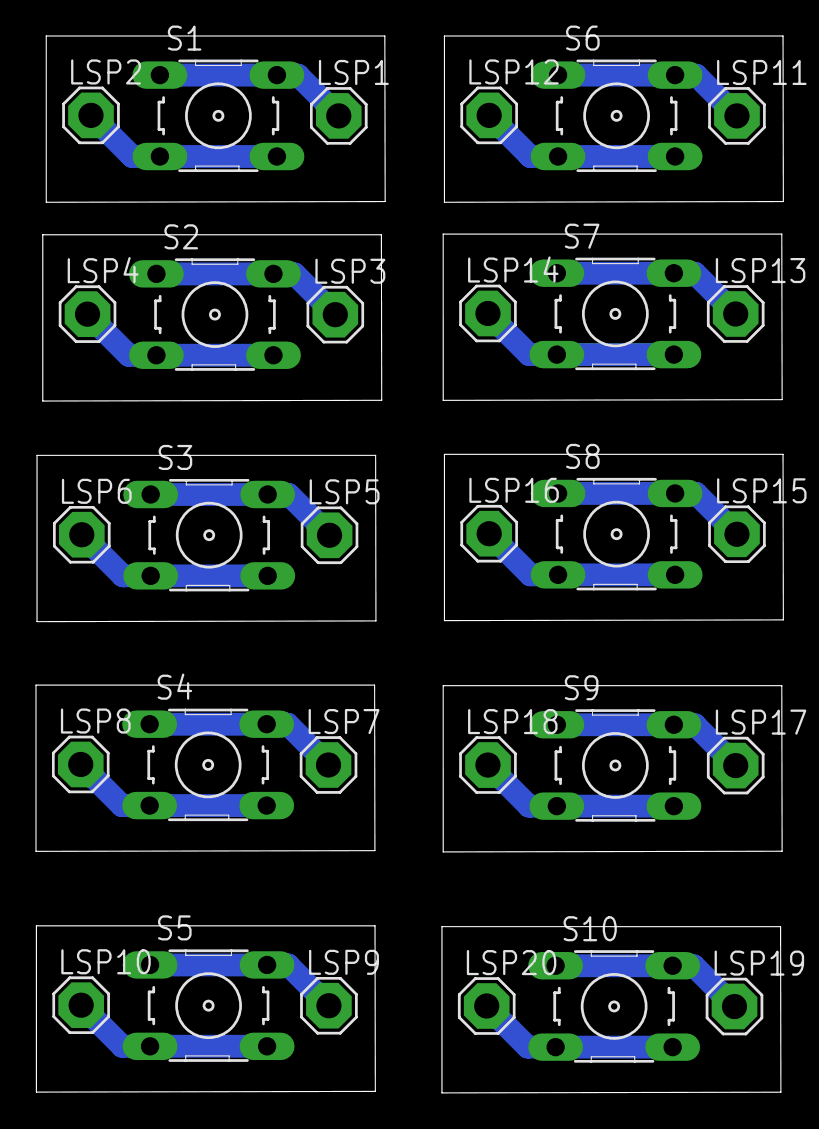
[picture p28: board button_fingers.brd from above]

Board: 2 copper layers, 41.5 x 58.7 mm, 30 parts (0 on the bottom side), 20 nets.

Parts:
LSP1, LSP2, LSP3, LSP4, LSP5, LSP6, LSP7, LSP8, LSP9, LSP10, LSP11, LSP12, LSP13, LSP14, LSP15, LSP16, LSP17, LSP18, LSP19, LSP20: SE14
S1, S2, S3, S4, S5, S6, S7, S8, S9, S10: B3F-10XX

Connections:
unnamed: LSP1.MP, S1.1, S1.2
unnamed: LSP2.MP, S1.3, S1.4
unnamed: LSP3.MP, S2.1, S2.2
unnamed: LSP4.MP, S2.3, S2.4
unnamed: LSP5.MP, S3.1, S3.2
unnamed: LSP6.MP, S3.3, S3.4
unnamed: LSP7.MP, S4.1, S4.2
unnamed: LSP8.MP, S4.3, S4.4
unnamed: LSP9.MP, S5.1, S5.2
unnamed: LSP10.MP, S5.3, S5.4
unnamed: LSP11.MP, S6.1, S6.2
unnamed: LSP12.MP, S6.3, S6.4
unnamed: LSP13.MP, S7.1, S7.2
unnamed: LSP14.MP, S7.3, S7.4
unnamed: LSP15.MP, S8.1, S8.2
unnamed: LSP16.MP, S8.3, S8.4
unnamed: LSP17.MP, S9.1, S9.2
unnamed: LSP18.MP, S9.3, S9.4
unnamed: LSP19.MP, S10.1, S10.2
unnamed: LSP20.MP, S10.3, S10.4

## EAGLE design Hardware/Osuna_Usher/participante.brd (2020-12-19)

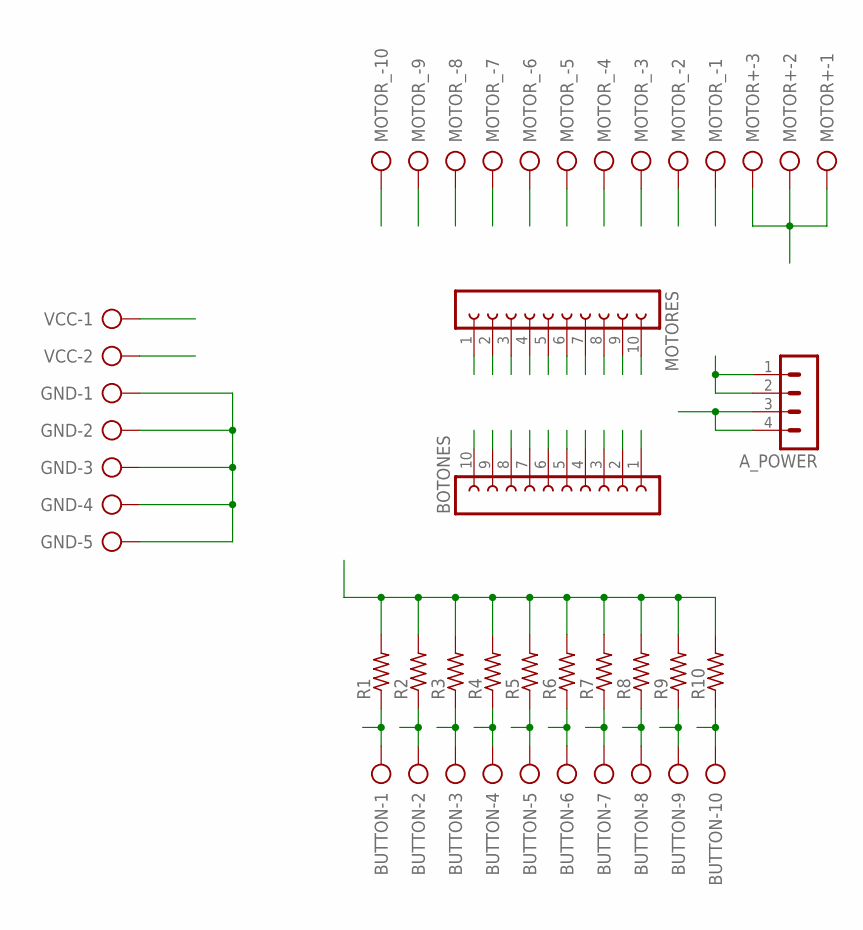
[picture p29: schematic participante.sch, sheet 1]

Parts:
A_POWER: MA04-1
BOTONES: FE10-1; FE10
BUTTON: AK300/10
GND: AK300/5
MOTOR+: AK300/3
MOTORES: FE10-1; FE10
MOTOR_: AK300/10
R1, R2, R3, R4, R5, R6, R7, R8, R9, R10: R-US_0204/7; 0204/7
VCC: AK300/2

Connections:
5VDC: R1.2, R2.2, R3.2, R4.2, R5.2, R6.2, R7.2, R8.2, R9.2, R10.2; also elsewhere on the board
A22: BOTONES.1, BUTTON.1, R1.1
A23: BOTONES.2, BUTTON.2, R2.1
A24: BOTONES.3, BUTTON.3, R3.1
A25: BOTONES.4, BUTTON.4, R4.1
A26: BOTONES.5, BUTTON.5, R5.1
A27: BOTONES.6, BUTTON.6, R6.1
A28: BOTONES.7, BUTTON.7, R7.1
A29: BOTONES.8, BUTTON.8, R8.1
A30: BOTONES.9, BUTTON.9, R9.1
A31: BOTONES.10, BUTTON.10, R10.1
AM_1: MOTORES.1; also elsewhere on the board
AM_2: MOTORES.2; also elsewhere on the board
AM_3: MOTORES.3; also elsewhere on the board
AM_4: MOTORES.4; also elsewhere on the board
AM_5: MOTORES.5; also elsewhere on the board
AM_6: MOTORES.6; also elsewhere on the board
AM_7: MOTORES.7; also elsewhere on the board
AM_8: MOTORES.8; also elsewhere on the board
AM_9: MOTORES.9; also elsewhere on the board
AM_10: MOTORES.10; also elsewhere on the board
GND: A_POWER.1, A_POWER.2, GND.1, GND.2, GND.3, GND.4, GND.5; also elsewhere on the board
M_N1: MOTOR_.1; also elsewhere on the board
M_N2: MOTOR_.2; also elsewhere on the board
M_N3: MOTOR_.3; also elsewhere on the board
M_N4: MOTOR_.4; also elsewhere on the board
M_N5: MOTOR_.5; also elsewhere on the board
M_N6: MOTOR_.6; also elsewhere on the board
M_N7: MOTOR_.7; also elsewhere on the board
M_N8: MOTOR_.8; also elsewhere on the board
M_N9: MOTOR_.9; also elsewhere on the board
M_N10: MOTOR_.10; also elsewhere on the board
VCC: MOTOR+.1, MOTOR+.2, MOTOR+.3, VCC.2; also elsewhere on the board
VCC_A: A_POWER.3, A_POWER.4, VCC.1

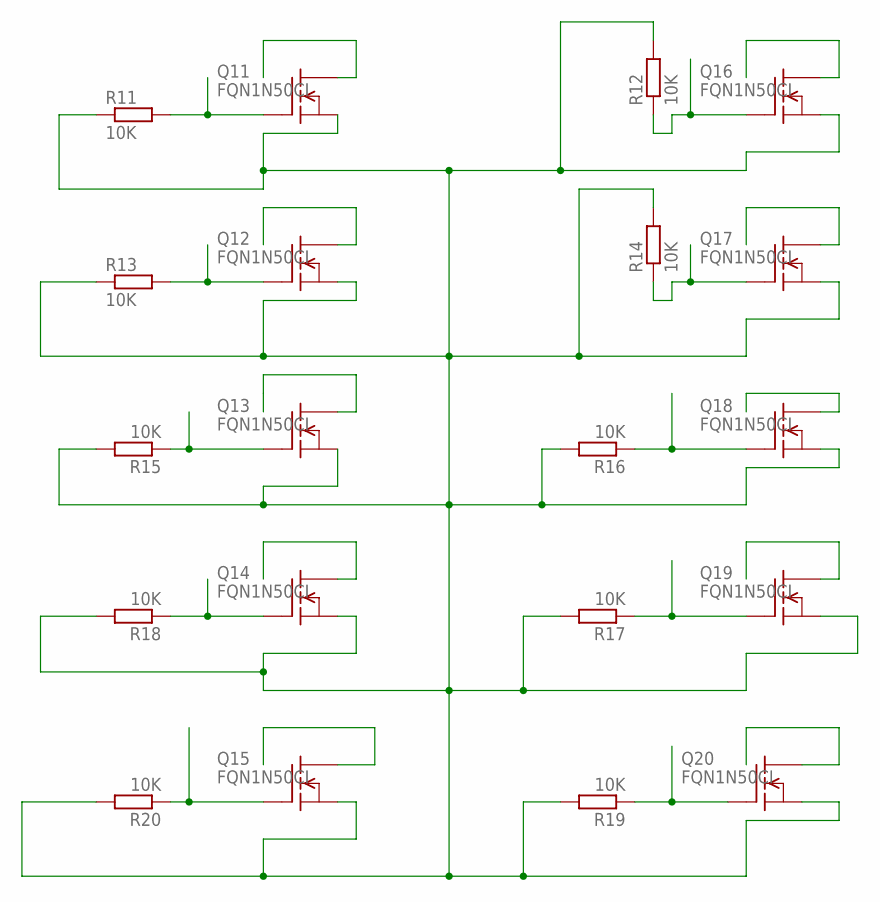
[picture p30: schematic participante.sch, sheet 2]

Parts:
Q11, Q12, Q13, Q14, Q15, Q16, Q17, Q18, Q19, Q20: FQN1N50CI; TO92-INLINE
R11, R12, R13, R14, R15, R16, R17, R18, R19, R20: 10K; 0207/10

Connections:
AM_1: Q11.2 (G), R11.2; also elsewhere on the board
AM_2: Q12.2 (G), R13.2; also elsewhere on the board
AM_3: Q13.2 (G), R15.1; also elsewhere on the board
AM_4: Q14.2 (G), R18.1; also elsewhere on the board
AM_5: Q15.2 (G), R20.1; also elsewhere on the board
AM_6: Q20.2 (G), R19.1; also elsewhere on the board
AM_7: Q19.2 (G), R17.1; also elsewhere on the board
AM_8: Q18.2 (G), R16.1; also elsewhere on the board
AM_9: Q17.2 (G), R14.1; also elsewhere on the board
AM_10: Q16.2 (G), R12.1; also elsewhere on the board
GND: Q11.3 (S), Q12.3 (S), Q13.3 (S), Q14.3 (S), Q15.3 (S), Q16.3 (S), Q17.3 (S), Q18.3 (S), Q19.3 (S), Q20.3 (S), R11.1, R12.2, R13.1, R14.2, R15.2, R16.2, R17.2, R18.2, R19.2, R20.2; also elsewhere on the board
M_N1: Q11.1 (D); also elsewhere on the board
M_N2: Q12.1 (D); also elsewhere on the board
M_N3: Q13.1 (D); also elsewhere on the board
M_N4: Q14.1 (D); also elsewhere on the board
M_N5: Q15.1 (D); also elsewhere on the board
M_N6: Q16.1 (D); also elsewhere on the board
M_N7: Q17.1 (D); also elsewhere on the board
M_N8: Q18.1 (D); also elsewhere on the board
M_N9: Q19.1 (D); also elsewhere on the board
M_N10: Q20.1 (D); also elsewhere on the board

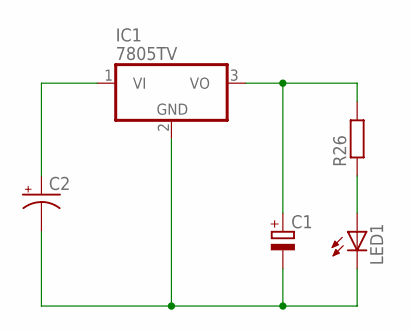
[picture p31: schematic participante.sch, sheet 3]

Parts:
C1: CPOL-EUE2.5-6; E2,5-6
C2: CPOL-USE3.5-8; E3,5-8
IC1: 7805TV; TO220V
LED1: LED5MM
R26: R-EU_0207/10; 0207/10

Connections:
5VDC: C1.+, IC1.3 (VO), R26.2; also elsewhere on the board
GND: C1.-, C2.-, IC1.2 (GND), LED1.K (C); also elsewhere on the board
unnamed: LED1.A, R26.1
VCC: C2.+, IC1.1 (VI); also elsewhere on the board

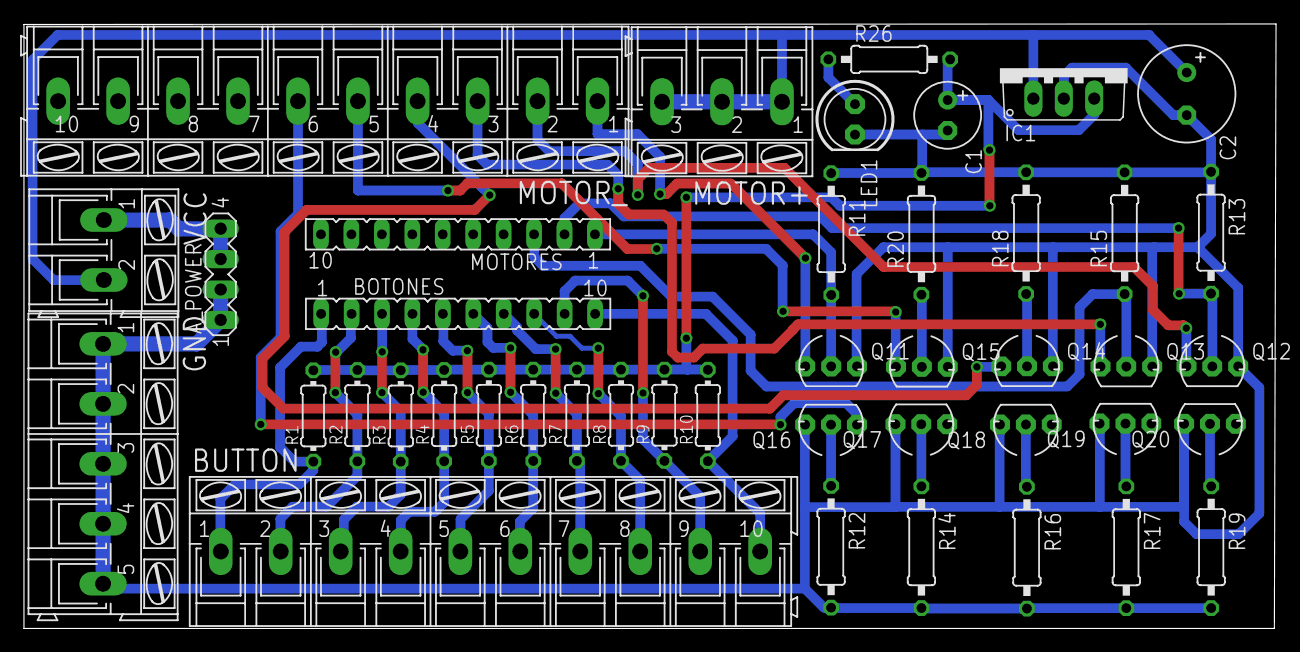
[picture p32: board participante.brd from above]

Board: 2 copper layers, 104.5 x 50.4 mm, 43 parts (0 on the bottom side), 35 nets.

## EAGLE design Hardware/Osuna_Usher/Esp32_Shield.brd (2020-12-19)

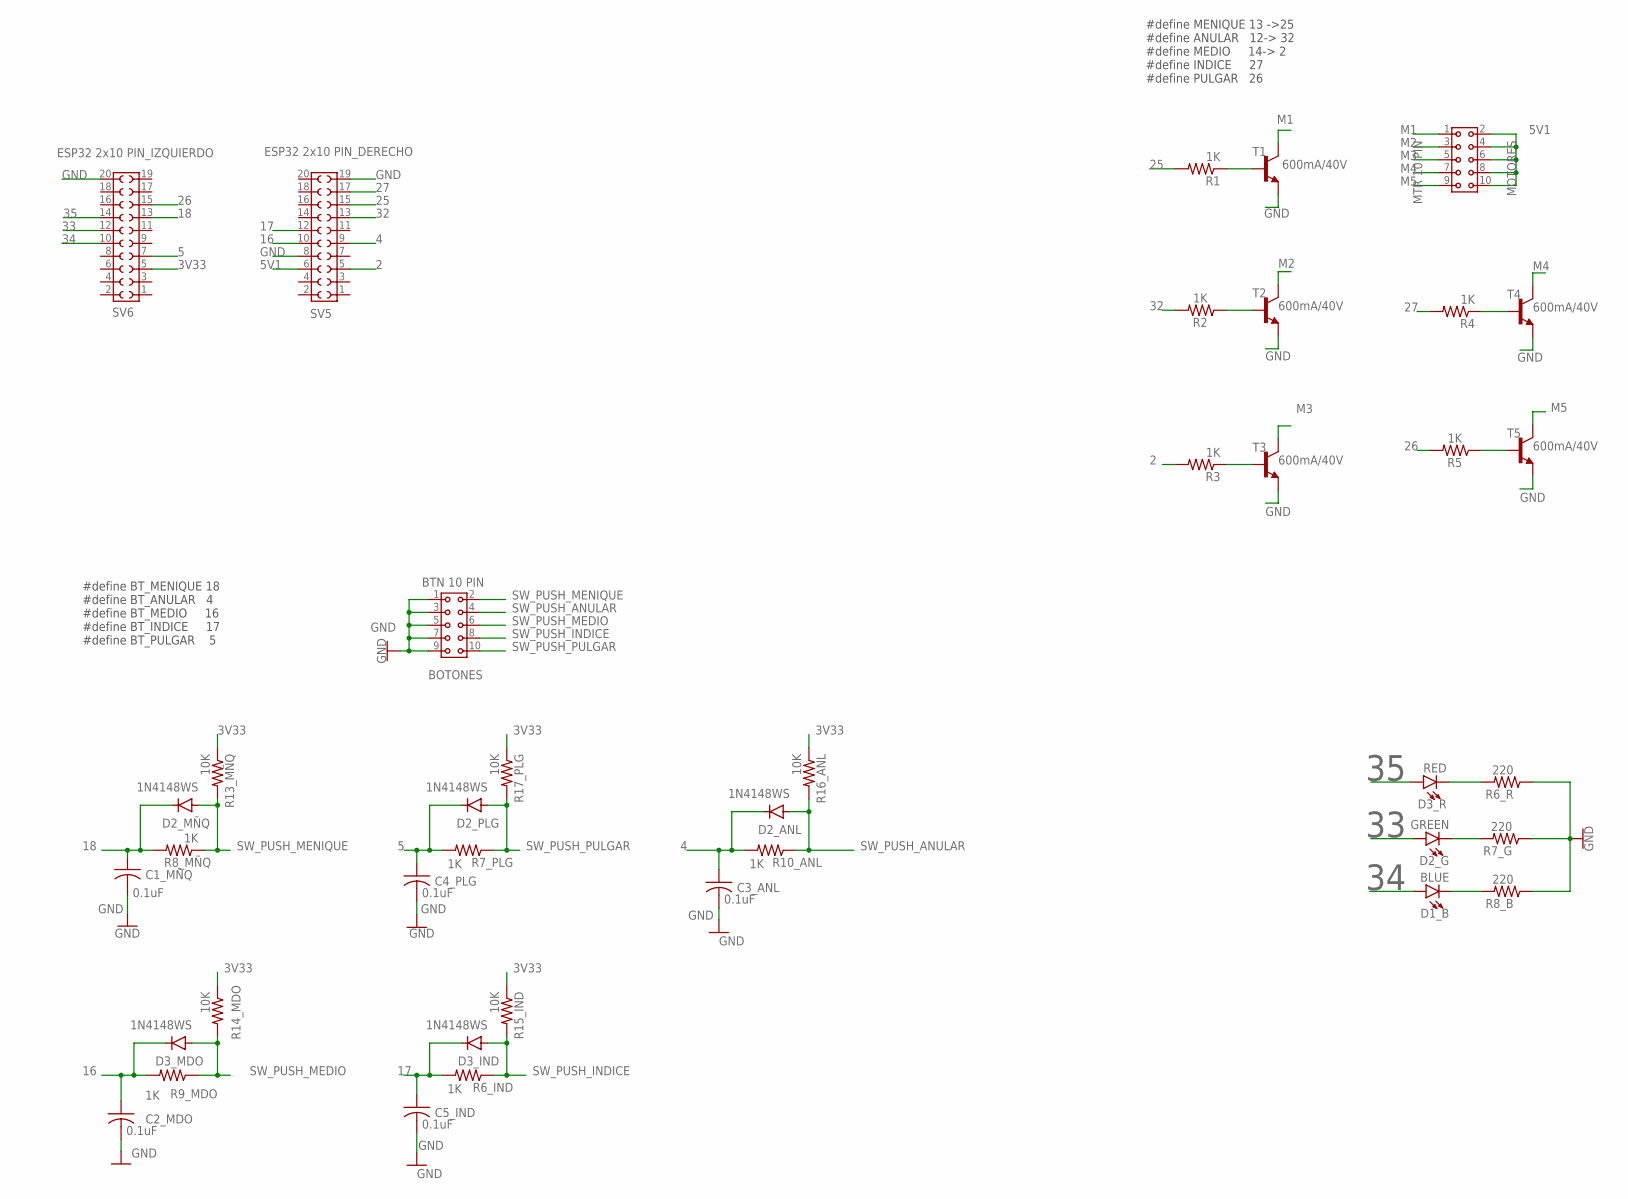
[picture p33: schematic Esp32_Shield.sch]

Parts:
BOTONES: BTN 10 PIN; 61301021821
C1_MÑQ, C2_MDO, C3_ANL, C4_PLG, C5_IND: 0.1uF; C0805
D1_B: BLUE; LED-1206
D2_ANL, D2_MÑQ, D2_PLG, D3_IND, D3_MDO: 1N4148WS; SOD-323
D2_G: GREEN; LED-1206
D3_R: RED; LED-1206
MOTORES: MTR 10 PIN; 61301021821
R1, R2, R3, R4, R5, R6_IND, R7_PLG, R8_MÑQ, R9_MDO, R10_ANL: 1K; R0805
R6_R, R7_G, R8_B: 220; R0805
R13_MÑQ, R14_MDO, R15_IND, R16_ANL, R17_PLG: 10K; R0805
SV5: ESP32 2x10 PIN_DERECHO; 61302021821
SV6: ESP32 2x10 PIN_IZQUIERDO; 61302021821
T1, T2, T3, T4, T5: 600mA/40V; SOT23-3

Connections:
2: R3.2, SV5.5
3V33: R13_MÑQ.1, R14_MDO.1, R15_IND.1, R16_ANL.1, R17_PLG.1, SV6.5
4: C3_ANL.1, D2_ANL.C, R10_ANL.2, SV5.9
5: C4_PLG.1, D2_PLG.C, R7_PLG.2, SV6.7
5V1: MOTORES.2, MOTORES.4, MOTORES.6, MOTORES.8, MOTORES.10, SV5.6
16: C2_MDO.1, D3_MDO.C, R9_MDO.2, SV5.10
17: C5_IND.1, D3_IND.C, R6_IND.2, SV5.12
18: C1_MÑQ.1, D2_MÑQ.C, R8_MÑQ.2, SV6.13
25: R1.2, SV5.15
26: R5.2, SV6.15
27: R4.2, SV5.17
32: R2.2, SV5.13
33: D2_G.A, SV6.12
34: D1_B.A, SV6.10
35: D3_R.A, SV6.14
GND: BOTONES.1, BOTONES.3, BOTONES.5, BOTONES.7, BOTONES.9, C1_MÑQ.2, C2_MDO.2, C3_ANL.2, C4_PLG.2, C5_IND.2, R6_R.1, R7_G.1, R8_B.1, SV5.8, SV5.19, SV6.20, T1.2 (E), T2.2 (E), T3.2 (E), T4.2 (E), T5.2 (E)
M1: MOTORES.1, T1.3 (C)
M2: MOTORES.3, T2.3 (C)
M3: MOTORES.5, T3.3 (C)
M4: MOTORES.7, T4.3 (C)
M5: MOTORES.9, T5.3 (C)
unnamed: R2.1, T2.1 (B)
unnamed: R1.1, T1.1 (B)
unnamed: R3.1, T3.1 (B)
unnamed: D3_R.C, R6_R.2
unnamed: D2_G.C, R7_G.2
unnamed: D1_B.C, R8_B.2
unnamed: R4.1, T4.1 (B)
unnamed: R5.1, T5.1 (B)
SW_PUSH_ANULAR: BOTONES.4, D2_ANL.A, R10_ANL.1, R16_ANL.2
SW_PUSH_INDICE: BOTONES.8, D3_IND.A, R6_IND.1, R15_IND.2
SW_PUSH_MEDIO: BOTONES.6, D3_MDO.A, R9_MDO.1, R14_MDO.2
SW_PUSH_MENIQUE: BOTONES.2, D2_MÑQ.A, R8_MÑQ.1, R13_MÑQ.2
SW_PUSH_PULGAR: BOTONES.10, D2_PLG.A, R7_PLG.1, R17_PLG.2

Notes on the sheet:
#define MENIQUE 13 ->25 #define ANULAR 12-> 32 #define MEDIO 14-> 2 #define INDICE 27 #define PULGAR 26
#define BT_MENIQUE 18 #define BT_ANULAR 4 #define BT_MEDIO 16 #define BT_INDICE 17 #define BT_PULGAR 5


Board: 2 copper layers, 46.2 x 33.5 mm, 40 parts (0 on the bottom side), 34 nets.

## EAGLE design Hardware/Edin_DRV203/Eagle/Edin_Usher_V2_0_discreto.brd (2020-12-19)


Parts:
LEFT: TINYPICO_HEADER_10NO_SILK_PTH_FEMALE; 1X10_NO_SILK
LOGO1: OSHW-LOGOS; OSHW-LOGO-S
MOTORES: MTR 10 PIN; 61301021821
RIGHT: TINYPICO_HEADER_10NO_SILK_PTH_FEMALE; 1X10_NO_SILK

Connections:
3.3V: LEFT.4; also elsewhere on the board
GND: LEFT.2, RIGHT.10; also elsewhere on the board
GPIO4: LEFT.5; also elsewhere on the board
GPIO5: RIGHT.4
GPIO14: LEFT.6; also elsewhere on the board
GPIO15: LEFT.7; also elsewhere on the board
GPIO18: RIGHT.3; also elsewhere on the board
GPIO19: RIGHT.2; also elsewhere on the board
GPIO21: RIGHT.6; also elsewhere on the board
GPIO22: RIGHT.5; also elsewhere on the board
GPIO23: RIGHT.1; also elsewhere on the board
GPIO25: LEFT.10
GPIO26: LEFT.9
GPIO27: LEFT.8; also elsewhere on the board
GPIO32: RIGHT.7
GPIO33: RIGHT.8
MTR1_-V5: MOTORES.1; also elsewhere on the board
MTR2_-V5: MOTORES.3; also elsewhere on the board
MTR3_-V5: MOTORES.5; also elsewhere on the board
MTR4_-V5: MOTORES.7; also elsewhere on the board
MTR5_-V5: MOTORES.9; also elsewhere on the board
RESET: RIGHT.9; also elsewhere on the board
USB: LEFT.3
VBAT: LEFT.1, MOTORES.2, MOTORES.4, MOTORES.6, MOTORES.8, MOTORES.10

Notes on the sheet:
TinyPICO Headers
#define MENIQUE 32 #define ANULAR 5 #define MEDIO 18 #define INDICE 19 #define PULGAR 23 #define EN 33


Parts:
BOTONES: BTN 10 PIN; 61301021821
C8: 0603B104K160CT; CAPC1608X87N
IC4: MAX6818EAP+T; SOP65P778X199-20N
S1: MOMENTARY-SWITCH-SPST-SMD-6.0X3.5MM; TACTILE_SWITCH_SMD_6.0X3.5MM

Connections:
3.3V: C8.1, IC4.20 (VCC); also elsewhere on the board
GND: BOTONES.1, BOTONES.3, BOTONES.5, BOTONES.7, C8.2, IC4.1 (!EN), IC4.10 (GND), S1.1; also elsewhere on the board
GPIO4: IC4.19 (OUT1); also elsewhere on the board
GPIO14: IC4.18 (OUT2); also elsewhere on the board
GPIO15: IC4.17 (OUT3); also elsewhere on the board
GPIO27: IC4.16 (OUT4); also elsewhere on the board
RESET: S1.2; also elsewhere on the board
SW_PUSH_ANULAR: BOTONES.4, IC4.4 (IN3)
SW_PUSH_INDICE: BOTONES.8, IC4.2 (IN1)
SW_PUSH_MEDIO: BOTONES.6, IC4.3 (IN2)
SW_PUSH_MENIQUE: BOTONES.2, IC4.5 (IN4)

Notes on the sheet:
#define BT_MENIQUE 27 #define BT_ANULAR 15 #define BT_MEDIO 14 #define BT_INDICE 4

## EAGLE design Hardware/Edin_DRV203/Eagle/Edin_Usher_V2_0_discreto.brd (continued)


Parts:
Q1: MMBT3904,215; SOT95P230X110-3N
Q2, Q3: BCM56DSF; SOT95P275X110-6N
R1: R-US_R0402; R0402
RN2: CAY10-102J4LF; CAY10102J4LF

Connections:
GND: Q1.2 (E), Q2.4 (E2), Q2.5 (E1), Q3.4 (E2), Q3.5 (E1); also elsewhere on the board
GPIO18: RN2.A3; also elsewhere on the board
GPIO19: RN2.A4; also elsewhere on the board
GPIO21: RN2.A1; also elsewhere on the board
GPIO22: RN2.A2; also elsewhere on the board
GPIO23: R1.1; also elsewhere on the board
MTR1_-V5: Q2.6 (C1); also elsewhere on the board
MTR2_-V5: Q2.3 (C2); also elsewhere on the board
MTR3_-V5: Q3.6 (C1); also elsewhere on the board
MTR4_-V5: Q3.3 (C2); also elsewhere on the board
MTR5_-V5: Q1.3 (C); also elsewhere on the board
unnamed: Q1.1 (B), R1.2
unnamed: Q2.1 (B1), RN2.B1
unnamed: Q2.2 (B2), RN2.B2
unnamed: Q3.1 (B1), RN2.B3
unnamed: Q3.2 (B2), RN2.B4


Board: 2 copper layers, 35.6 x 33.7 mm, 14 parts (1 on the bottom side), 27 nets.

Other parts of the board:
LOGO2: OSHW-LOGOS; OSHW-LOGO-S

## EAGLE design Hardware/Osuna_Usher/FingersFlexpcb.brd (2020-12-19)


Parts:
J1, J3: 6100XX21121_61001021121; 61001021121
J1_ANULAR, J3_MEDIO, J5_INDICE, J7_MEÑIQUE: 62000311121
J2_ANULAR, J4_MEDIO, J6_INDICE, J8_MEÑIQUE, J9_PULGAR, J10_PULGAR: CONN_01; 1X01
M1_ANULAR, M2_MEDIO, M3_INDICE, M4_MEÑIQUE: MOTOR10MM; VIBE-MOTOR-10MM

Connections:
BTN_DEDO_ANULAR: J1_ANULAR.1, J2_ANULAR.1
BTN_DEDO_INDICE: J5_INDICE.1, J6_INDICE.1
BTN_DEDO_MEDIO: J3_MEDIO.1, J4_MEDIO.1
GND: J1_ANULAR.3, J3_MEDIO.3, J5_INDICE.3, J7_MEÑIQUE.3, J9_PULGAR.1, J10_PULGAR.1, M1_ANULAR.-, M2_MEDIO.-, M3_INDICE.-, M4_MEÑIQUE.-
MTR_ANULAR: J1_ANULAR.2, M1_ANULAR.+
MTR_INDICE: J5_INDICE.2, M3_INDICE.+
MTR_MEDIO: J3_MEDIO.2, M2_MEDIO.+
MTR_MEÑIQUE: J7_MEÑIQUE.2, M4_MEÑIQUE.+
unnamed: J7_MEÑIQUE.1, J8_MEÑIQUE.1


Board: 2 copper layers, 208.3 x 131.8 mm, 16 parts (0 on the bottom side), 9 nets.

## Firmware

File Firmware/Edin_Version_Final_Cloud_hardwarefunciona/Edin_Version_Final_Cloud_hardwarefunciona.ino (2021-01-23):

/**Attached interrupts
  *GPIO27   --->    SW_PUSH_MENIQUE
  *GPIO15   --->    SW_PUSH_ANULAR
  *GPIO14   --->    SW_PUSH_MEDIO
  *GPIO04   --->    SW_PUSH_INDICE
  ***********
  *PWM MOTORS 
  * GPIO23    --->    MTR_5
  * GPIO19    --->    MTR_4
  * GPIO18    --->    MTR_3
  * GPIO05    --->    MTR_2
  * GPIO32    --->    MTR_1
  * GPIO33    --->    ENABLE
  * 
   */
  

// PubNub MQTT example using ESP32.
#include <WiFi.h>
#include <ArduinoJson.h>                                                                                  //----------------------------JSON Arduino Library
#include <PubSubClient.h>
#include <TinyPICO.h>
#include "settings.h"

TinyPICO tp = TinyPICO();

//*****************************************************************************Definicion de Variables Globales
String Sipaddrs = "000.000.000.000";
uint32_t chipId = 0;                                                                                      //variable donde se alamacena el identificador de cliente para el servicio de MQTT (OJO Este debe ser un identificador unico para cada dispositivo fisico sino se reiniciara el servidor MQTT)
int retry = 0;                                                                                            //variable donde se almacenan los intentos de conexion fallidos
char id_de_operacion[20];

//******************************************************************************FSM Settings
bool mesgrecv = false;
static enum {STATE_IDLE, STATE_PREGUNTA, STATE_TRANSMIT_RESPUESTA} fsm_state = STATE_IDLE;

//******************************************************************************Variables de mensaje desde concentrador MQTT para motores. 

int motor_channel, motor_time, motor_effect;

int idOperation       = 0;
int idModule          = 0;
int gloveCode         = 0;
int answer            = 0;

//******************************************************************************Variables de Botones. 
struct boton {
  const uint8_t PIN;
  uint32_t numberKeyPresses;
  volatile bool pressed;
};

boton btn_4 = {4 ,0, false};
boton btn_3 = {14, 0, false};
boton btn_2 = {15, 0, false};
boton btn_1 = {27, 0, false};

void IRAM_ATTR isr_btn1(){
  btn_1.numberKeyPresses += 1;
  btn_1.pressed = true;
}

void IRAM_ATTR isr_btn2(){
  btn_2.numberKeyPresses += 1;
  btn_2.pressed = true;
}

void IRAM_ATTR isr_btn3(){
  btn_3.numberKeyPresses += 1;
  btn_3.pressed = true;
}

void IRAM_ATTR isr_btn4(){
  btn_4.numberKeyPresses += 1;
  btn_4.pressed = true;
}


//*****************************************************************************Variables de Motores

// Pin para inicio y frenado de Motores
int enable1Pin = 33; 
volatile bool EnablePinState;

 
// Propiedades de PWM que funcionan ocn driver y motores. 
const int freq = 3000;
const int resolution = 8;

uint16_t  dutyCyclefull = 255;
uint16_t  dutyCycleHalf = 95;
uint16_t  dutyCycleLow = 15;
uint16_t  initDutyCycle = 0;

uint16_t  clickTime = 0;

//******************************************************************************Estructura de puertos a Motores 
struct vmotor {
  const uint8_t motorPin;     //Puerto fisico al que se encuntra cableado el puerto de PWM del Chip DRV2603
  const uint8_t pwmChannel;  //Canal logico de comunicaciones para el puerto
};

//Mapa de asignacion de puertos y canales para PWM ver esquematico para confirmar puertos.

vmotor MTR_5 = {23, 4}; //GPIO23 canal 4
vmotor MTR_4 = {19, 3}; //GPIO19 canal 3
vmotor MTR_3 = {18, 2}; //GPIO18 canal 2
vmotor MTR_2 = {5,  1}; //GPIO5 canal 1
vmotor MTR_1 = {32, 0}; //GPIO32 canal 0

//*******************************************************************************Funcion de PWM para puerto 32 y 33 del ESP32
void aPinMode(int pinNum, int pinDir) {
  // Enable GPIO32 or 33 as output. 
  if (pinNum == 32 || pinNum == 33) {
    uint64_t gpioBitMask = (pinNum == 32) ? 1ULL<<GPIO_NUM_32 : 1ULL<<GPIO_NUM_33;
    gpio_mode_t gpioMode = (pinDir == OUTPUT) ? GPIO_MODE_OUTPUT : GPIO_MODE_INPUT;
    gpio_config_t io_conf;
    io_conf.intr_type = GPIO_INTR_DISABLE;
    io_conf.mode = gpioMode;
    io_conf.pin_bit_mask = gpioBitMask;
    io_conf.pull_down_en = GPIO_PULLDOWN_DISABLE;
    io_conf.pull_up_en = GPIO_PULLUP_DISABLE;
    gpio_config(&io_conf);
  } else pinMode(pinNum, pinDir);
}


void operation (byte* payloadrsp){
  Serial.println(F("mensaje recibido de topico operacion"));
  tp.DotStar_SetPixelColor( 0xFFC900 );
  const int capacity = JSON_OBJECT_SIZE(1);
  StaticJsonDocument<capacity> edin_operation_json;
  
  DeserializationError err = deserializeJson(edin_operation_json, payloadrsp);
  
  if (err) {
    Serial.print(F("deserializeJson() failed with code "));
    Serial.println(err.c_str());
    return;
  }

  strlcpy(id_de_operacion, edin_operation_json["idOperation"] | "idOperation", 20);
  
  Serial.print("idOperation: ");
  Serial.println(id_de_operacion);

  tp.DotStar_Clear();
  fsm_state = STATE_PREGUNTA;       
}

void callback(char* topic, byte* payload, unsigned int length) {
  String payload_buff;
  for (int i=0;i<length;i++) {
    payload_buff = payload_buff+String((char)payload[i]);
  }
  Serial.println(payload_buff); // Print out messages.
  
  if (strcmp (rebootTopic, topic) == 0) {                                                                 //verificar si el topico conicide con el Topico rebootTopic[] definido en el archivo settings.h local
    Serial.println(F("Rebooting in 5 seconds..."));                                                                    //imprimir mensaje de Aviso sobre reinicio remoto de unidad.
    delay(5000);
    ESP.restart();                                                                                          //Emitir comando de reinicio para ESP32
  }
  
  if (strcmp (operationTopic, topic) == 0) {                                                                 //verificar si el topico conicide con el Topico updateTopic[] definido en el archivo settings.h local
    operation(payload);                                                                                //enviar a la funcion handleUpdate el contenido del mensaje para su parseo.
  }   
}


WiFiClient MQTTclient;
PubSubClient client(mqttServer, mqttPort, callback, MQTTclient);


long lastReconnectAttempt = 0;

boolean reconnect() {
  if (client.connect(clientId,"edin","edin")) {
    client.subscribe(rebootTopic); // Subscribe to channel.
    client.subscribe(operationTopic); // Subscribe to channel.    
  }
  return client.connected();
}

//**********************************************************************************Get Chip ID*********************************************************************************
void GloveID(){
  for(int i=0; i<17; i=i+8) {
    chipId |= ((ESP.getEfuseMac() >> (40 - i)) & 0xff) << i;
  }
  
  Serial.printf("ESP32 Chip model = %s Rev %d\n", ESP.getSdkVersion(), ESP.getChipRevision());
  Serial.printf("This chip has %d cores\n", ESP.getFlashChipSpeed());
  Serial.print("Chip ID: "); Serial.println(chipId);
  
  delay(3000);
}
void configuration_json (){
  const int capacity = JSON_OBJECT_SIZE(10);
  StaticJsonDocument<capacity> edin_json_config_doc;
  // create an object
  JsonObject object = edin_json_config_doc.to<JsonObject>();

  object["AliveUpdate:hrs"]   = isalivemsg_interval/3600000;
  object["MqttServer"]        = mqttServer;
  char buf[16];
  sprintf(buf, "IP:%d.%d.%d.%d", WiFi.localIP()[0], WiFi.localIP()[1], WiFi.localIP()[2], WiFi.localIP()[3] );
  Serial.println(String(buf));
  object["MqttPort"]          = mqttPort;
  object["gloveCode"]         = chipId ;
  object["IpNodo"]            = String (buf);
  object["ClientID"]          = String(clientId);
    
  String output;
  size_t n = serializeJson(object, output);                                                                  //SAve CPU cycles by calculatinf the size.
  Serial.println(F("publishing device manageTopic metadata:"));
  Serial.println(output);
  if (!client.connected()) {
    reconnect();
  }
  if (client.publish(responseTopic, output.c_str(), n)) {
    Serial.println(F("device Publish ok"));
  }else {
    Serial.println(F("device Publish failed:"));
  }

}
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

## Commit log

2020-08-31 ESP32 design files V3
    SMD components
    [Esp32_Shield V3 no LED.brd, Esp32_Shield V3 no LED.sch]
2020-09-01 documents updated
    Not the initial commit any more
    [06031C104KAT2A.stl, 06031C104KAT2A.stp, 0603B104K160CT.stl, 0603B104K160CT.stp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]
2020-09-03 STL files for ptrinting
    Printing.
    [EDIN_Tapadera.stl, EDIN_tapa.stl, Esp32_Shield V3 no LED.brd, Esp32_Shield V3 no LED.sch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]
2020-10-16 added FirmWare
    added FirmWare
    [Edin_Usher_V2_0.brd, Edin_Usher_V2_0.sch, Esp32_Shield V3 no LED.brd, Esp32_Shield V3 no LED.sch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]
2020-10-23 added Sistem configuration
    agregado un diagrama de configracion de sistema.
2020-12-19 Update to MVP versions
    Update repository to latest development.
    [Edin_TinyPico_Nano.brd, Edin_TinyPico_Nano.sch, Edin_Usher_DRV2630_reference_design.brd, Edin_Usher_DRV2630_reference_design.sch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]
2021-01-23 added Cloud tested Firmware version
    Se agrego la version provada del firmware hsata conexxion y recepcionde applicacion en la nube.
2021-08-02 node red POT to APP
    Node red flow to POST to WebAPP

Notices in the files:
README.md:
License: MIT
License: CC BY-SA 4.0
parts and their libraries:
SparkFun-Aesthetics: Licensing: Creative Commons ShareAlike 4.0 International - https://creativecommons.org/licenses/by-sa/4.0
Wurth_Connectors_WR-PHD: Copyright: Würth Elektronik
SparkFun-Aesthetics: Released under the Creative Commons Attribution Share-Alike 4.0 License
